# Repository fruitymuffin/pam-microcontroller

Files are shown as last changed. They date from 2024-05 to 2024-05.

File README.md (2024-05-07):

# pam-microcontroller
The AVR controller is based on the AVR64DA32 chip which is programmed via the UPDI interface.

## 1. Compiling
The C/C++ code is compiled using avr-gcc/avr-g++ and makes use of avr-libc. [Microchip Studio](https://www.microchip.com/en-us/tools-resources/develop/microchip-studio) was used as the IDE as it integrates the avr-g++ toolchain so building is easy.

## 2. Uploading
The serialUPDI interface was used to upload .hex or .elf files to the chip with the help of [avrdude](https://github.com/avrdudes/avrdude). An avrdude upload command can be added to Microchip Studio as a external tool to make uploading executables easier.
Go to Tools->External Tools and add a new tool. The tool was configured as:

Command:
```
C:\Program Files\avrdude-v7.3-windows-x64\avrdude.exe
```
Arguments:
```
-p avr64da32 -P COM5 -b 115200 -c serialupdi -C "C:\Program Files\avrdude-v7.3-windows-x64\avrdude.conf" -U flash:w:$(BinDir)\led-controller.hex:i
```

Initial Directory:
```
$(BinDir)
```

In order to set fuses with avrdude on the newer DA series chips, it was necessary to manually write it. Luckily the corrent fuse locations are specified in avrdude.conf under the DX family information. To enable the reset pin, the fuse was written by:
```
avrdude -c serialupdi -p avr64da32 -P com5 -U syscfg0:w:0xC8:m
```

## 3. Serial communication
The avr controller has a FTDI 230XS usb to serial chip. Which will typically show up as /dev/ttyUSBn on linux. To write to the port, we can open it as a file using fopen, however to do so we need to know which tty port our device is on. The device is not guaranteed to always be /dev/ttyUSB0.
To be able to access it consistently we can create a symlink to a known filename by creating a udev rule.

Create a file caled "N-my-rule.rules" in ```/etc/udev/rules.d/``` with the contents:
```
SUBSYSTEM=="tty", ATTRS{idVendor}=="0403", ATTRS{idProduct}=="6015", ATTRS{serial}=="DU0D13LG", SYMLINK+="ttypam-serial"
```

This creates a symlink called ```ttypam-serial``` to the tty port which matches the properties given (idVendor, idProduct, serial), so that we can now use ```/dev/ttypam-serial``` to access our device.

To get the required USB device info use:
```
udevadm info -a -n /dev/ttyUSB0 | grep '{serial}\|{idProduct}\|{idVendor}' | head -n3
```
Where ttyUSB0 is replaced with the tty port of the device. See ```lsusb```.

It might also be necessary to add the user to the dialout group to get permissions to usb devices.

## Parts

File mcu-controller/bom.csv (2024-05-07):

Reference | Value | Datasheet | Footprint | Qty | DNP
C1,C5,C6,C7,C12,C13,C15,C16,C17 | 0.1u | ~ | Capacitor_SMD:C_0805_2012Metric | 9
C2,C3 | 4.7u | ~ | Capacitor_SMD:C_0805_2012Metric | 2
C4 | 0.22u | ~ | Capacitor_SMD:C_0805_2012Metric | 1
C8 | 10u | ~ | Capacitor_SMD:C_1206_3216Metric | 1
C9,C10 | 47p | Tantalum | Capacitor_SMD:C_0805_2012Metric | 2
C11,C14 | 1u | ~ | Capacitor_SMD:C_0805_2012Metric | 2
D1 | LED | ~ | LED_SMD:LED_0805_2012Metric | 1
D2 | RXLED | ~ | LED_SMD:LED_0805_2012Metric | 1
D3 | TXLED | ~ | LED_SMD:LED_0805_2012Metric | 1
J1 | 0534260210 | ~ | Library:CON_534260210_MOL | 1
J2 | HR10A-7R-6SB(73) | ~ | Library:HR10A-7R-6SB(73) | 1
J3 | Conn_01x13 | ~ | Connector_PinHeader_2.54mm:PinHeader_1x13_P2.54mm_Vertical | 1
J4 | 0534260610 | ~ | Library:CON_534260610_MOL | 1
J5,J6 | Conn_01x03 | ~ | Connector_PinHeader_2.54mm:PinHeader_1x03_P2.54mm_Vertical | 2
J7 | 65100516121 | ~ | Connector_USB:USB_Mini-B_Wuerth_65100516121_Horizontal | 1
R1 | 1k | ~ | Resistor_SMD:R_0805_2012Metric | 1
R2,R5 | 4.7k | ~ | Resistor_SMD:R_0805_2012Metric | 2
R3,R4 | 27 | ~ | Resistor_SMD:R_0805_2012Metric | 2
R6 | 10k | ~ | Resistor_SMD:R_0805_2012Metric | 1
R7 | 330 | ~ | Resistor_SMD:R_0805_2012Metric | 1
R8,R9 | 270 | ~ | Resistor_SMD:R_0805_2012Metric | 2
SW1 | SW_Push | ~ | Button_Switch_SMD:SW_SPST_FSMSM | 1
U1 | LM340SX-5.0 | https://www.analog.com/media/en/technical-documentation/data-sheets/112935ff.pdf | Package_TO_SOT_SMD:TO-263-3_TabPin2 | 1
U2 | FT230XS | https://www.ftdichip.com/Support/Documents/DataSheets/ICs/DS_FT230X.pdf | Package_SO:SSOP-16_3.9x4.9mm_P0.635mm | 1
U3 | MCP4822 | http://ww1.microchip.com/downloads/en/DeviceDoc/20002249B.pdf | Package_SO:SOIC-8_3.9x4.9mm_P1.27mm | 1
U4 | AVR64DA32x-xPT | https://ww1.microchip.com/downloads/en/DeviceDoc/AVR64DA28-32-48-64-Data-Sheet-40002233B.pdf | Package_QFP:TQFP-32_7x7mm_P0.8mm | 1

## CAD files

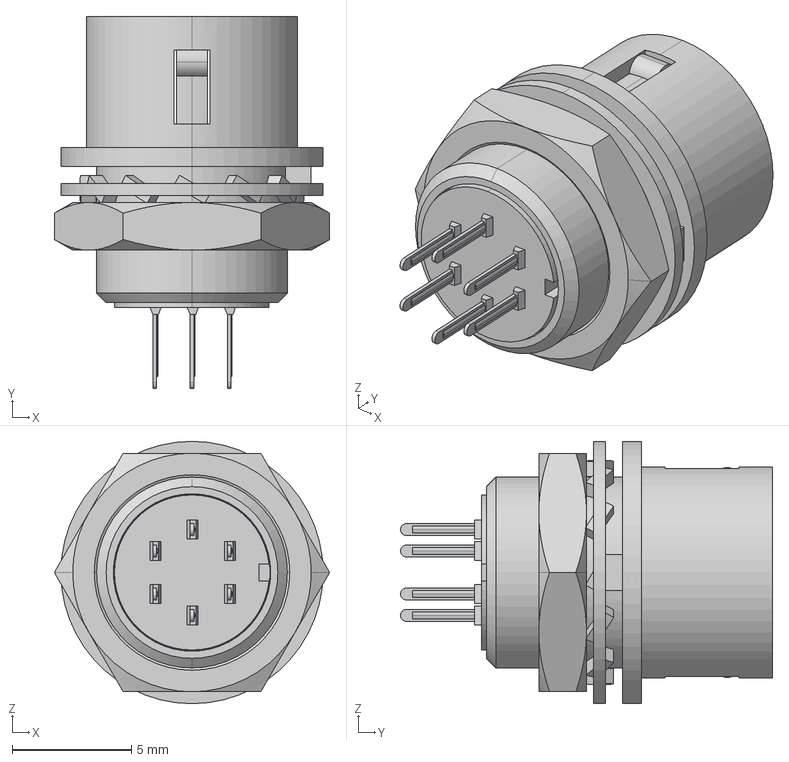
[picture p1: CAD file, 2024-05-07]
mcu-controller/models/HR10A-7R-6PB.stp
11.5 x 15.6 x 11.0 mm

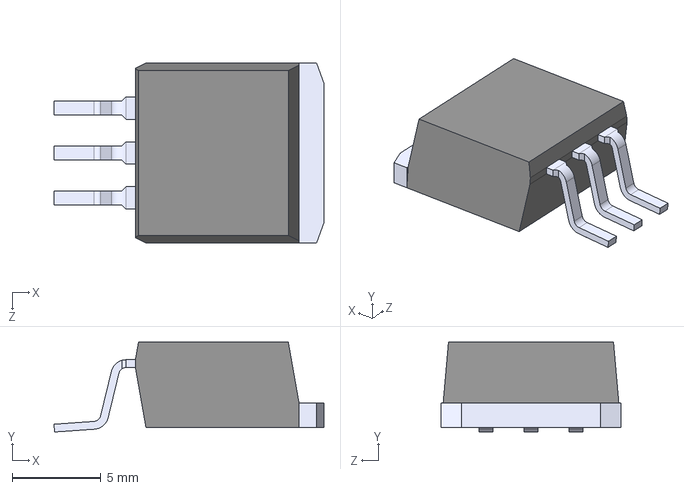
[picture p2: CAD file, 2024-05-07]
mcu-controller/models/LM340SX-5.0_NOPB.step
15.2 x 5.08 x 10.2 mm

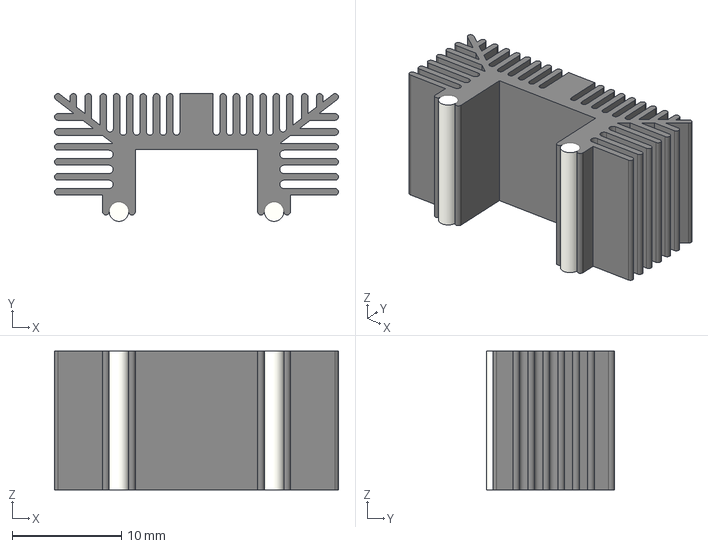
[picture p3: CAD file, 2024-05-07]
mcu-controller/models/ohmite_DA-T263-401E-TR.stp
26.0 x 11.7 x 12.7 mm

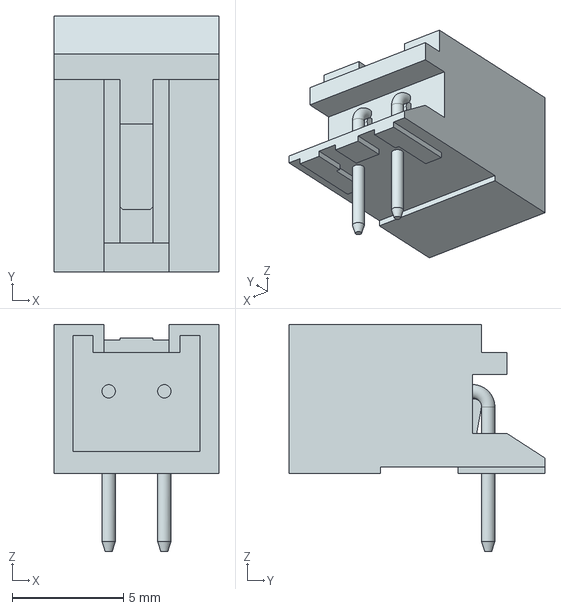
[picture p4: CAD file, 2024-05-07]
mcu-controller/models/534260210.stp
7.40 x 11.5 x 10.2 mm

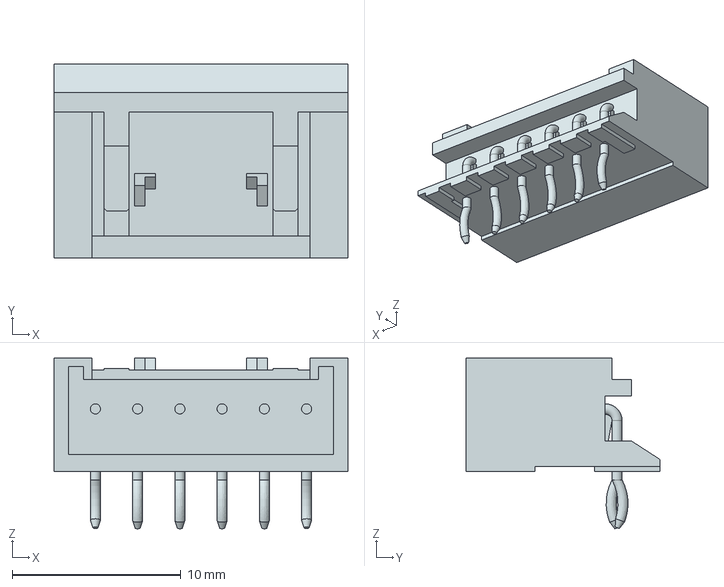
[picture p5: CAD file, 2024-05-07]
mcu-controller/models/534260610.stp
17.4 x 11.5 x 10.1 mm

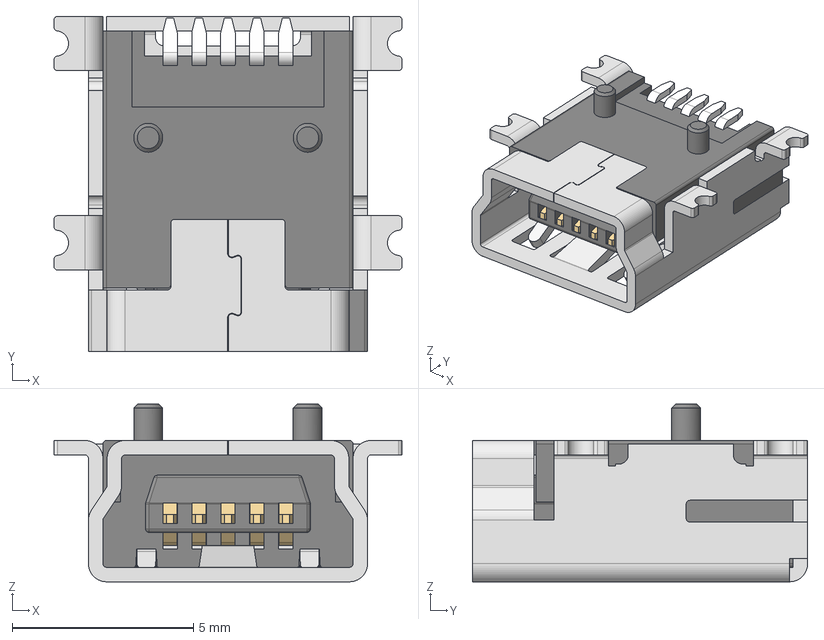
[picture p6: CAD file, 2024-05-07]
mcu-controller/models/65100516121.stp
9.60 x 9.25 x 4.90 mm
Shielding
Insulator
Pin_1 x 5

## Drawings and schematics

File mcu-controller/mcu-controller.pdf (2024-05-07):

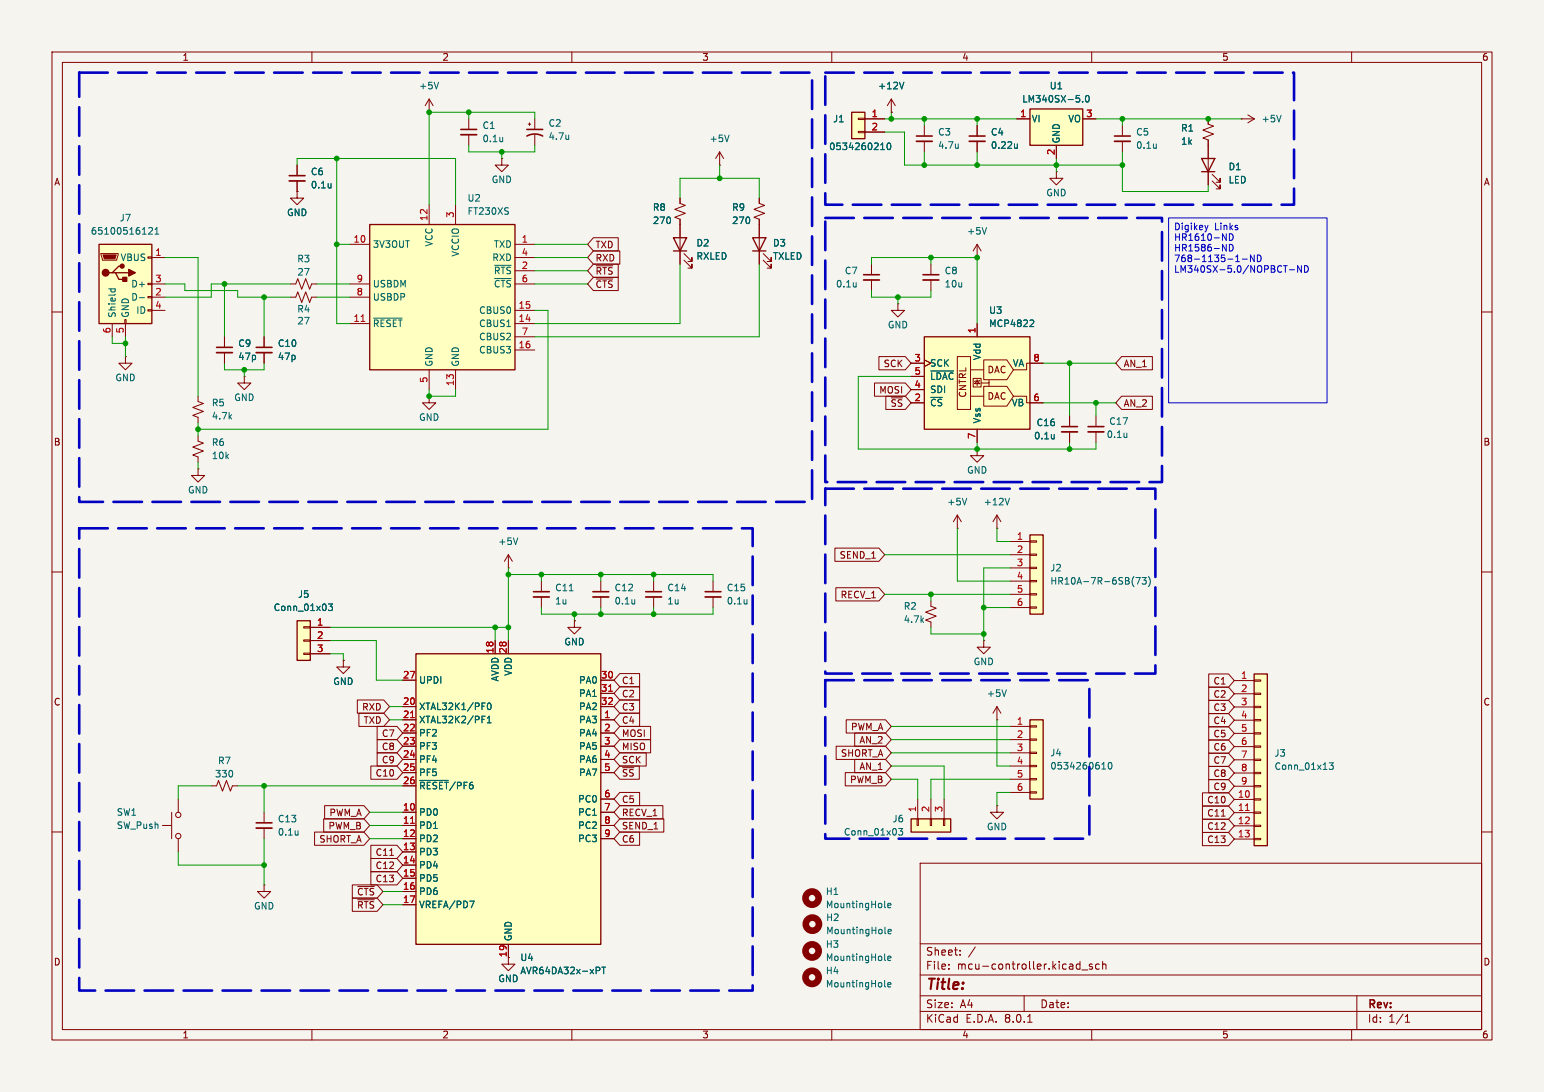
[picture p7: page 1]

1 ~{CS} 2 SCK 3 SDI 4 ~{LDAC} 5 VB 6 Vss 7 VA 8 +12V D1

1 ~{CS} 2 SCK 3 SDI 4 ~{LDAC} 5 VB 6 Vss 7 VA 8 U3 GND MCP4822 GND GND

Id: 1/1 Title: File: mcu-controller.kicad_sch Sheet: /

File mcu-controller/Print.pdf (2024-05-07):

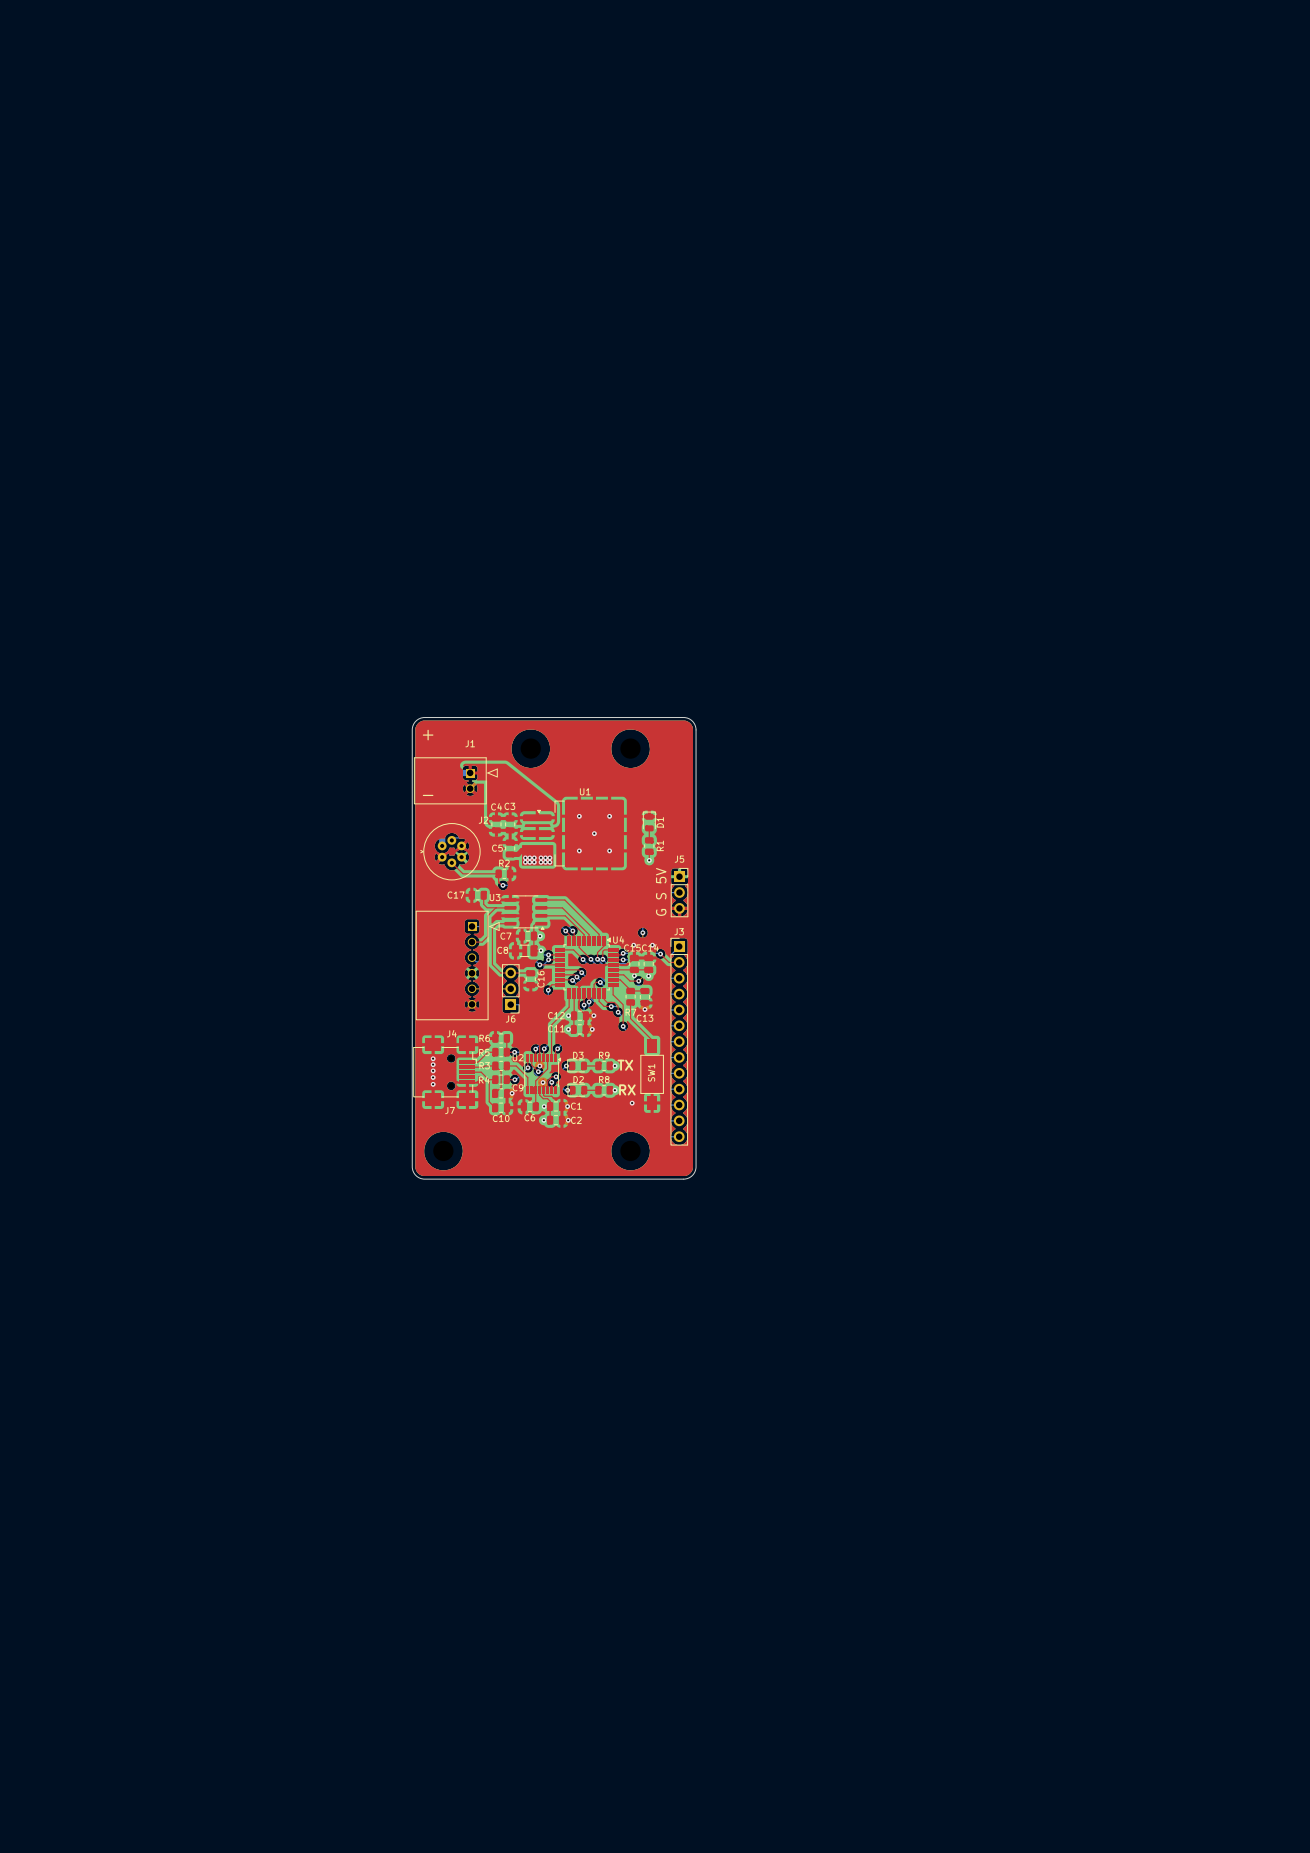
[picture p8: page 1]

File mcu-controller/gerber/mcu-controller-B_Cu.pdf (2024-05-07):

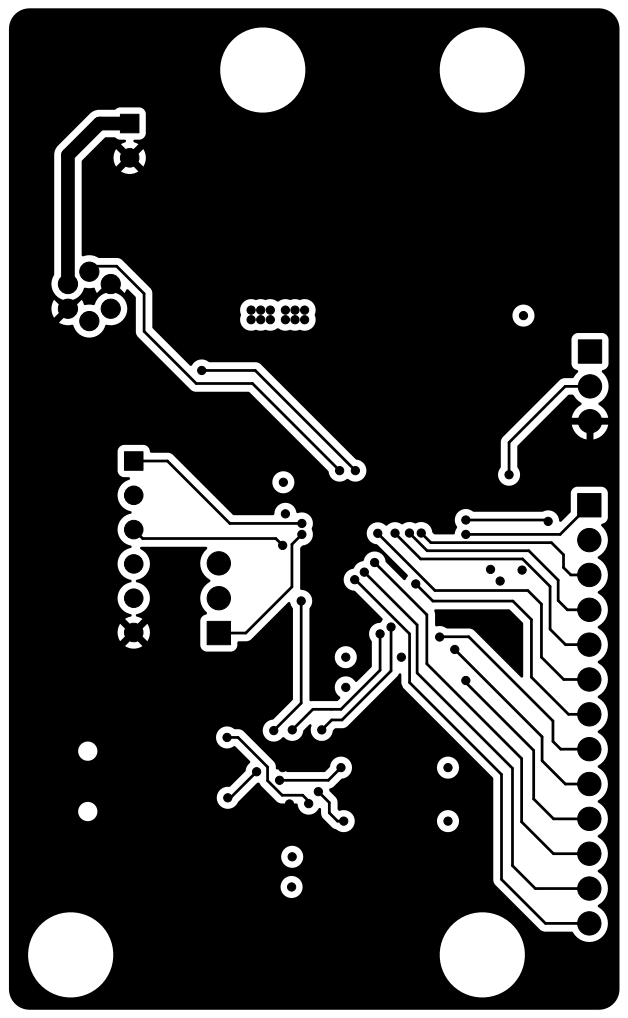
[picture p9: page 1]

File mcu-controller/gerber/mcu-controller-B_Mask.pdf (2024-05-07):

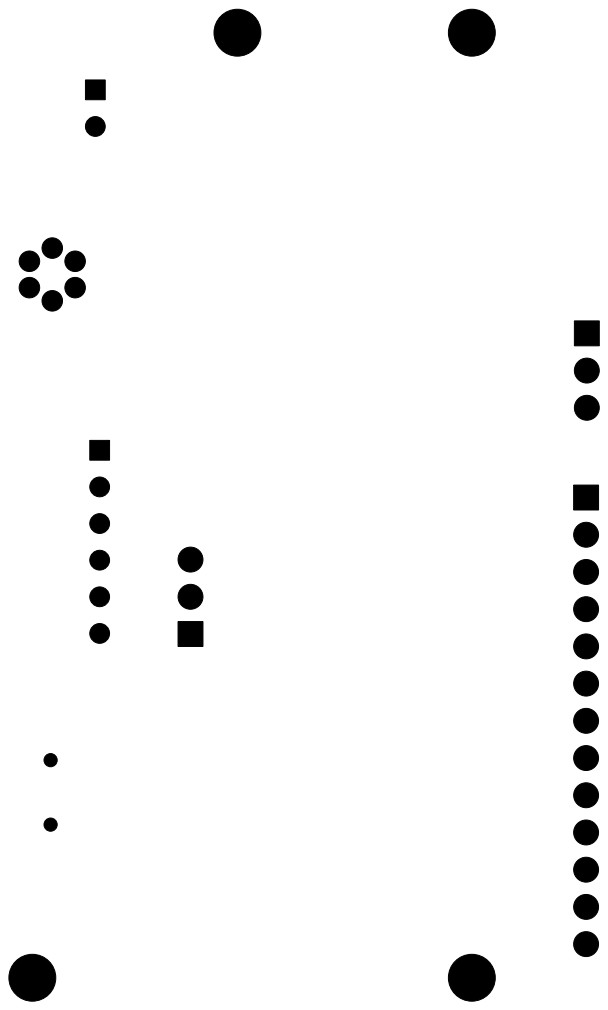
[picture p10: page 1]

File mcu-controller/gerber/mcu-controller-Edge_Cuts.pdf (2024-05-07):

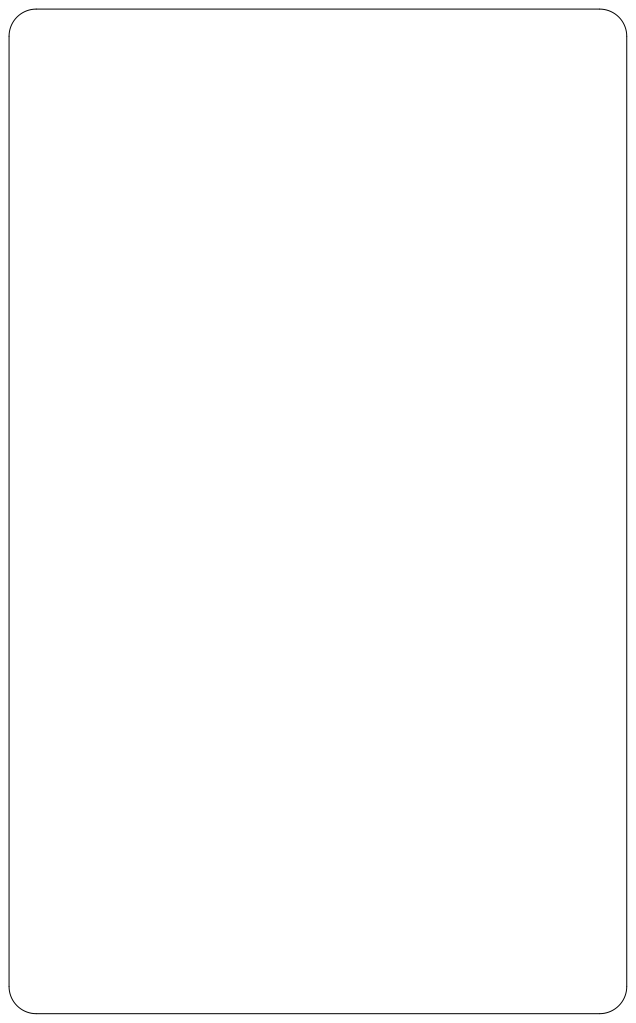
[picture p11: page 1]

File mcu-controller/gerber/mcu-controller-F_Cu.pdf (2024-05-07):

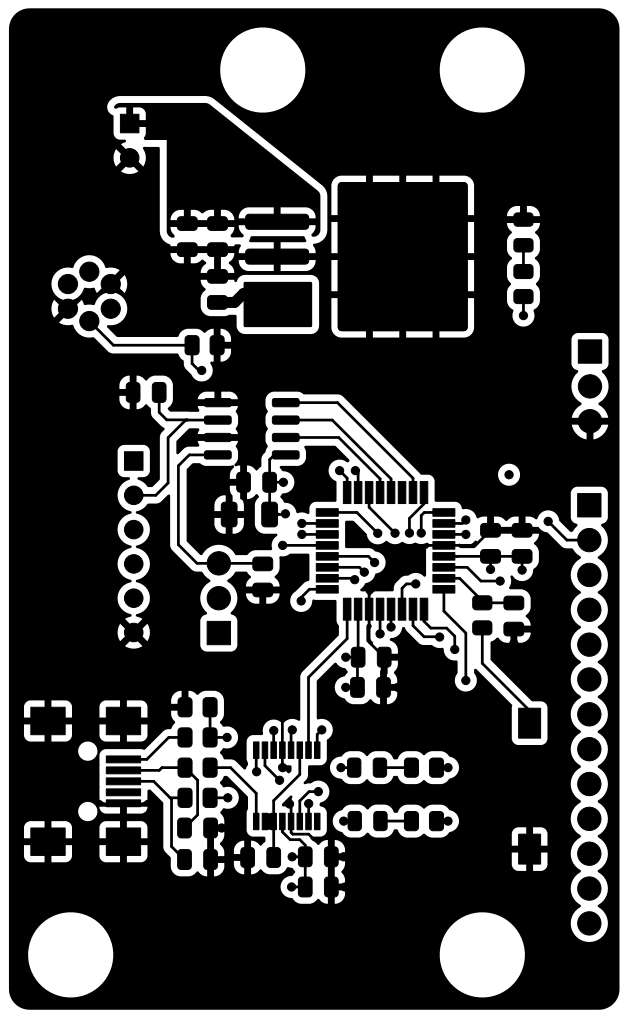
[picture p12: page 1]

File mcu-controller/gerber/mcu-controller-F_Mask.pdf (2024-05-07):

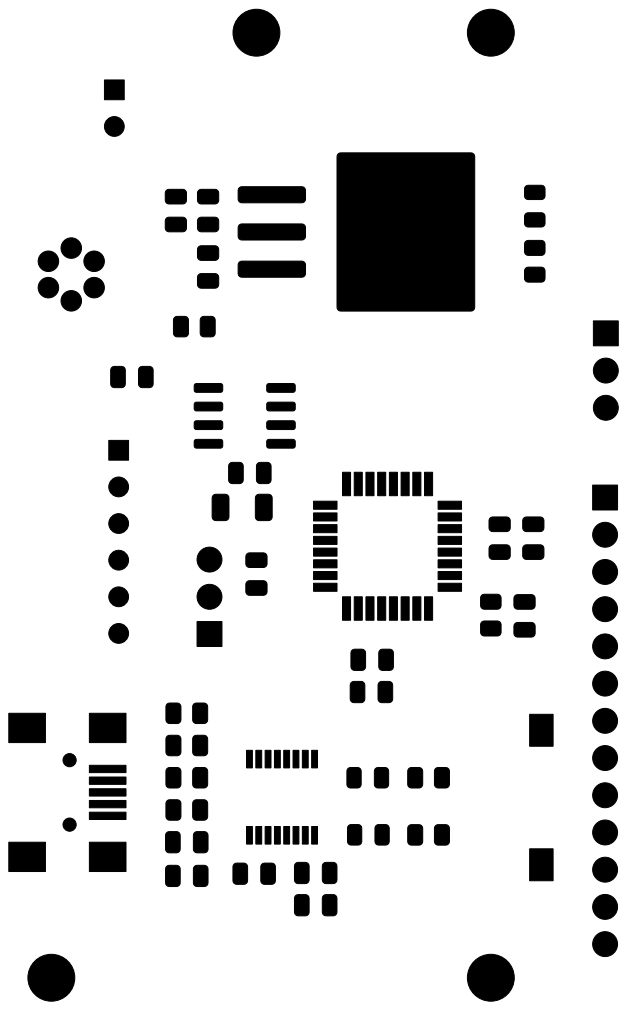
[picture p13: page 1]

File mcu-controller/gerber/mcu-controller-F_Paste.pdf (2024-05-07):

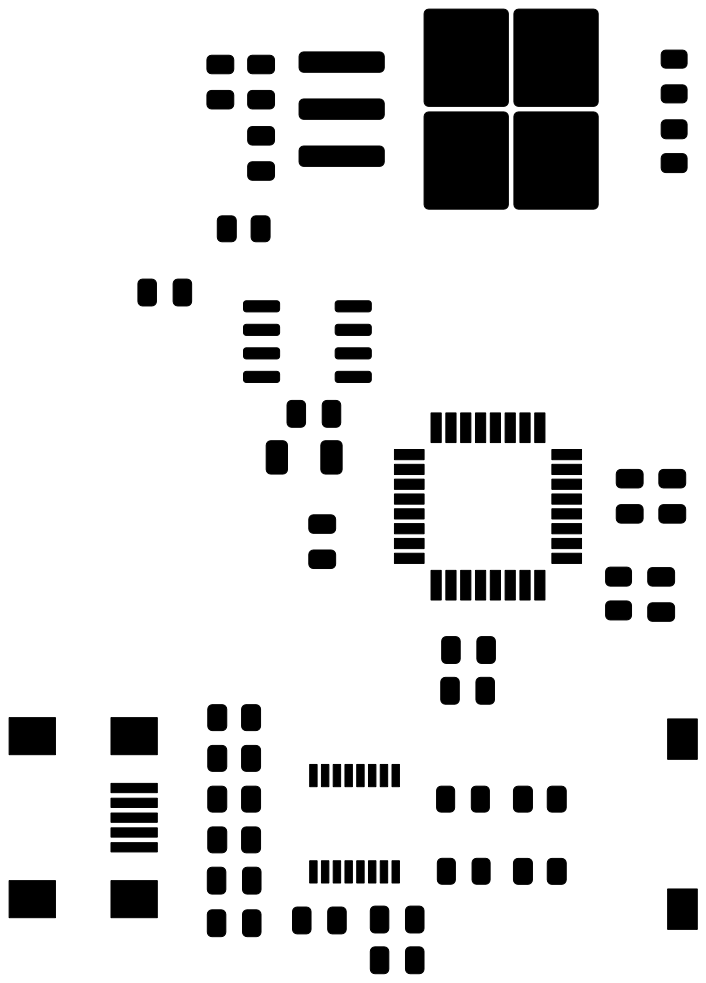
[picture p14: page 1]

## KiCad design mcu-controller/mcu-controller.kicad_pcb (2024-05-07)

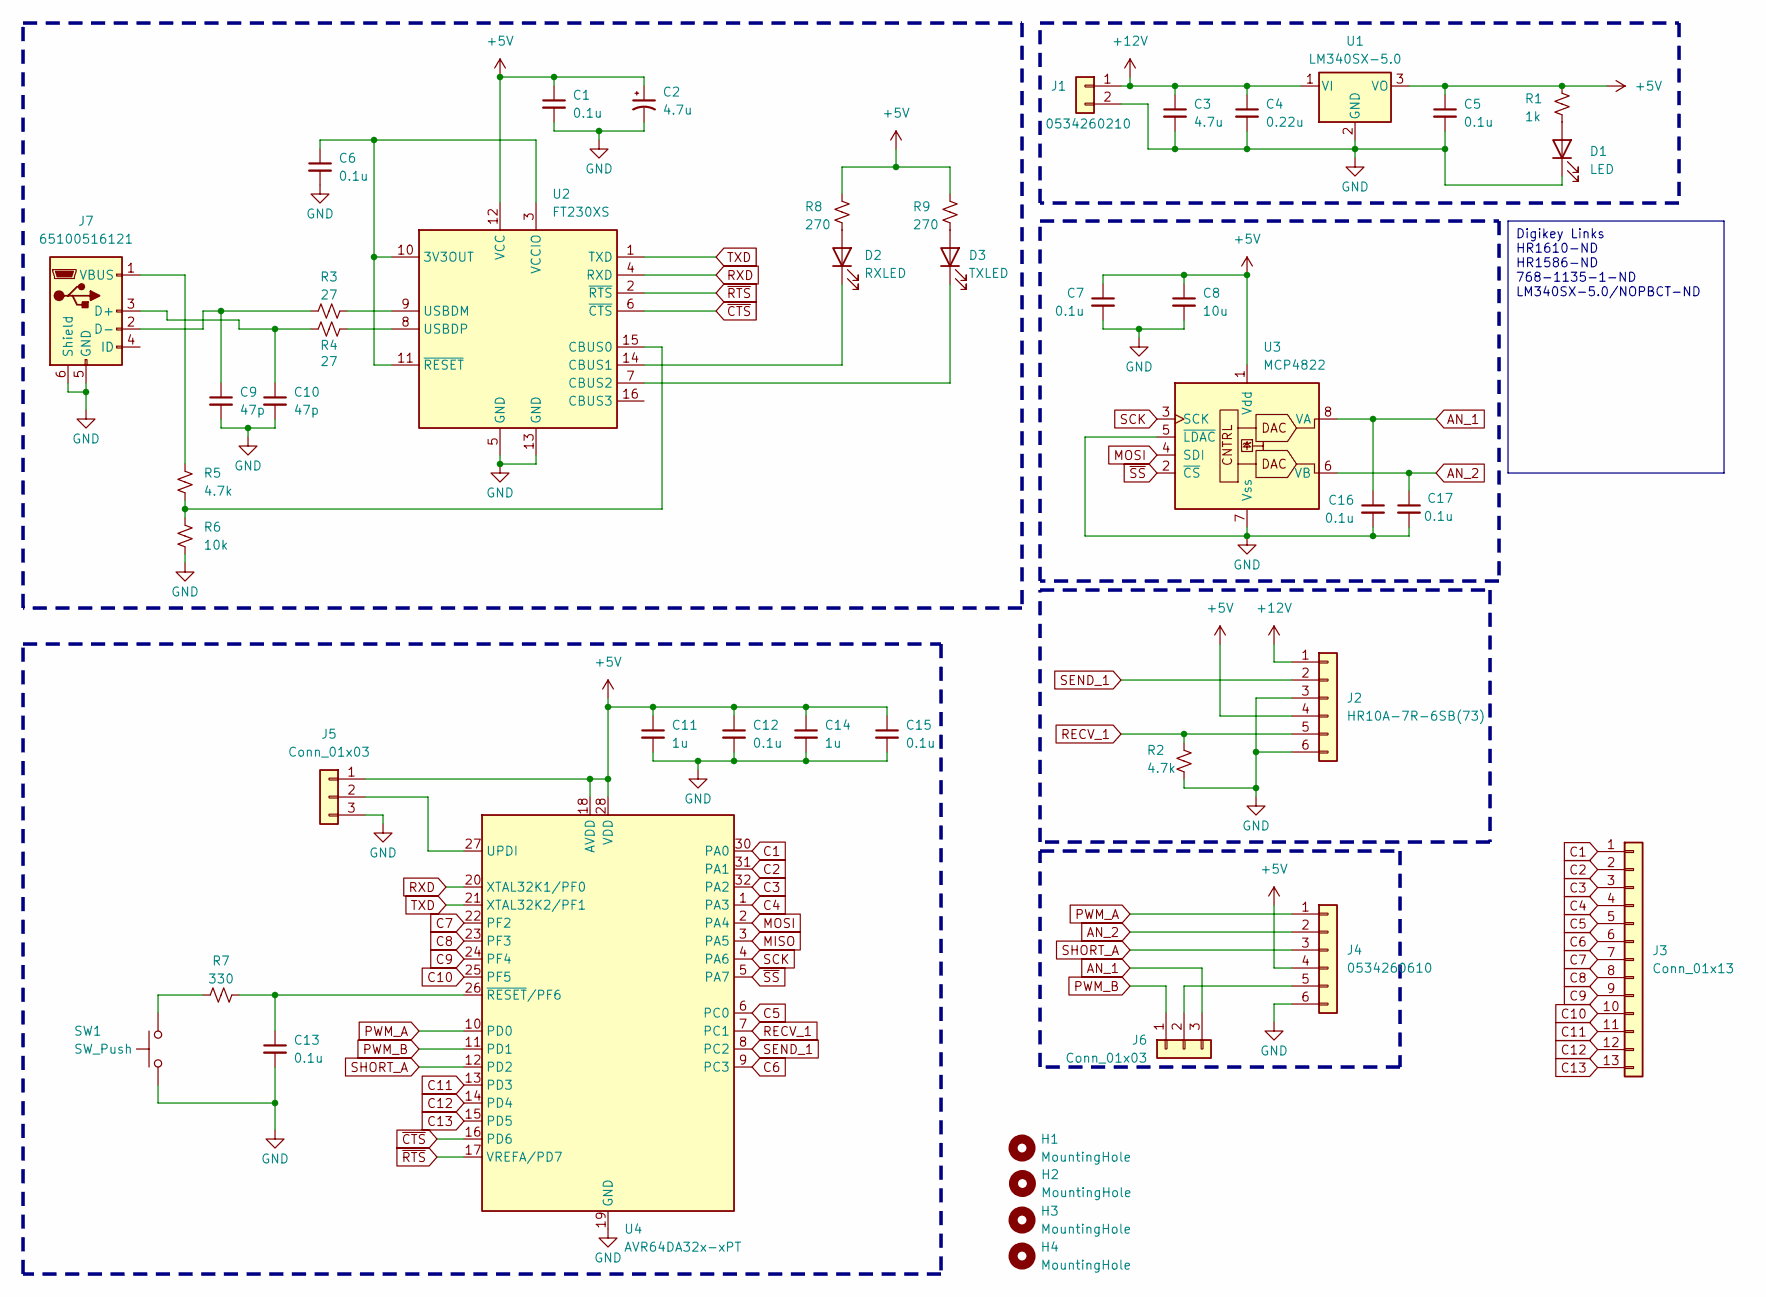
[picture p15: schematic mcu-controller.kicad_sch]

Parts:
C1, C5, C6, C7, C12, C13, C15, C16, C17: 0.1u; C_0805_2012Metric
C2, C3: 4.7u; C_0805_2012Metric
C4: 0.22u; C_0805_2012Metric
C8: 10u; C_1206_3216Metric
C9, C10: 47p; C_0805_2012Metric
C11, C14: 1u; C_0805_2012Metric
D1: LED; LED_0805_2012Metric
D2: RXLED; LED_0805_2012Metric
D3: TXLED; LED_0805_2012Metric
H1, H2, H3, H4: MountingHole; MountingHole_3.2mm_M3
J1: 0534260210; CON_534260210_MOL
J2: HR10A-7R-6SB(73)
J3: Conn_01x13; PinHeader_1x13_P2.54mm_Vertical
J4: 0534260610; CON_534260610_MOL
J5, J6: Conn_01x03; PinHeader_1x03_P2.54mm_Vertical
J7: 65100516121; USB_Mini-B_Wuerth_65100516121_Horizontal
R1: 1k; R_0805_2012Metric
R2, R5: 4.7k; R_0805_2012Metric
R3, R4: 27; R_0805_2012Metric
R6: 10k; R_0805_2012Metric
R7: 330; R_0805_2012Metric
R8, R9: 270; R_0805_2012Metric
SW1: SW_Push; SW_SPST_FSMSM
U1: LM340SX-5.0; TO-263-3_TabPin2
U2: FT230XS; SSOP-16_3.9x4.9mm_P0.635mm
U3: MCP4822; SOIC-8_3.9x4.9mm_P1.27mm
U4: AVR64DA32x-xPT; TQFP-32_7x7mm_P0.8mm

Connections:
+5V: C1.1, C2.1, C5.1, C7.1, C8.1, C11.1, C12.1, C14.1, C15.1, J2.4, J4.4, J5.1, R1.1, R8.1, R9.1, U1.3 (VO), U2.12 (VCC), U3.1 (Vdd), U4.18 (AVDD), U4.28 (VDD)
+12V: C3.1, C4.1, J1.1, J2.1, U1.1 (VI)
AN_1: C16.1, J6.3, U3.8 (VA)
AN_2: C17.1, J4.2, U3.6 (VB)
C1: J3.1, U4.30 (PA0)
C2: J3.2, U4.31 (PA1)
C3: J3.3, U4.32 (PA2)
C4: J3.4, U4.1 (PA3)
C5: J3.5, U4.6 (PC0)
C6: J3.6, U4.9 (PC3)
C7: J3.7, U4.22 (PF2)
C8: J3.8, U4.23 (PF3)
C9: J3.9, U4.24 (PF4)
C10: J3.10, U4.25 (PF5)
C11: J3.11, U4.13 (PD3)
C12: J3.12, U4.14 (PD4)
C13: J3.13, U4.15 (PD5)
GND: C1.2, C2.2, C3.2, C4.2, C5.2, C6.2, C7.2, C8.2, C9.2, C10.2, C11.2, C12.2, C13.2, C14.2, C15.2, C16.2, C17.2, D1.1 (K), J1.2, J2.3, J2.6, J4.6, J5.3, J7.5 (GND), J7.6 (Shield), R2.2, R6.2, SW1.1, U1.2 (GND), U2.5 (GND), U2.13 (GND), U3.5 (~LDAC), U3.7 (Vss), U4.19 (GND), U4.29 (GND)
MISO: U4.3 (PA5)
MOSI: U3.4 (SDI), U4.2 (PA4)
unnamed: D1.2 (A), R1.2
unnamed: D2.2 (A), R8.2
unnamed: D2.1 (K), U2.14 (CBUS1)
unnamed: D3.2 (A), R9.2
unnamed: D3.1 (K), U2.7 (CBUS2)
unnamed: J4.5, J6.2
unnamed: J5.2, U4.27 (UPDI)
unnamed: C10.1, J7.3 (D+), R4.1
unnamed: C9.1, J7.2 (D-), R3.1
unnamed: J7.1 (VBUS), R5.1
unnamed: R7.1, SW1.2
unnamed: C6.1, U2.3 (VCCIO), U2.10 (3V3OUT), U2.11 (~RESET)
unnamed: R5.2, R6.1, U2.15 (CBUS0)
unnamed: R3.2, U2.9 (USBDM)
unnamed: R4.2, U2.8 (USBDP)
unnamed: C13.1, R7.2, U4.26 (~RESET/PF6)
PWM_A: J4.1, U4.10 (PD0)
PWM_B: J6.1, U4.11 (PD1)
RECV_1: J2.5, R2.1, U4.7 (PC1)
RXD: U2.4 (RXD), U4.20 (XTAL32K1/PF0)
SCK: U3.3 (SCK), U4.4 (PA6)
SEND_1: J2.2, U4.8 (PC2)
SHORT_A: J4.3, U4.12 (PD2)
TXD: U2.1 (TXD), U4.21 (XTAL32K2/PF1)
~CTS: U2.6 (~CTS), U4.16 (PD6)
~RTS: U2.2 (~RTS), U4.17 (VREFA/PD7)
~SS: U3.2 (~CS), U4.5 (PA7)

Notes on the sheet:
Digikey Links HR1610-ND HR1586-ND 768-1135-1-ND LM340SX-5.0/NOPBCT-ND

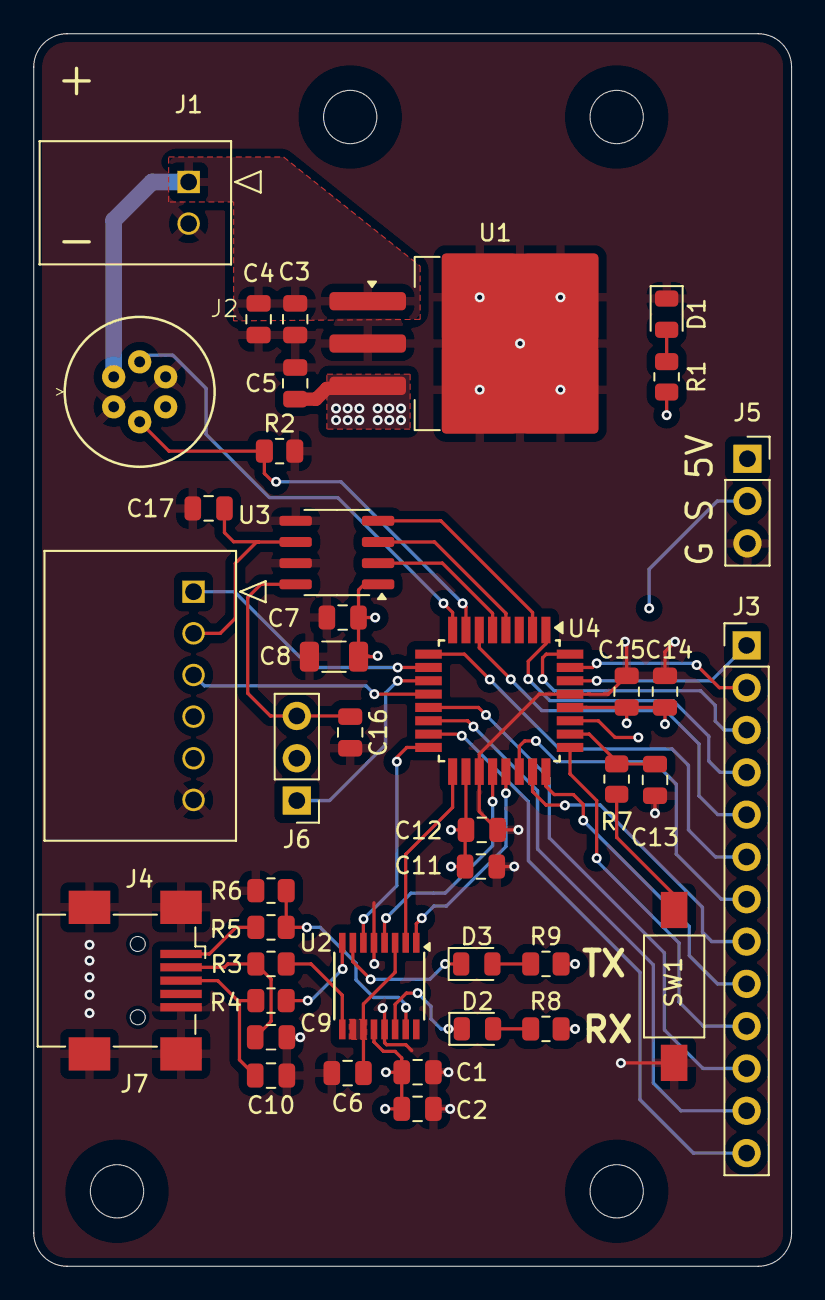
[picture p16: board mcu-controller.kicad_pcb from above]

Board: 4 copper layers, 45.5 x 74.0 mm, 45 parts (0 on the bottom side), 46 nets.

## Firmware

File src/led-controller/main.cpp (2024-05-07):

/*
 * led-controller.cpp
 *
 * Created: 16/04/2024 7:16:16 PM
 * Author : jmcna
 */ 

// Clock params
#define F_CPU 8000000UL

#include <avr/io.h>
#include <avr/interrupt.h>
#include <util/delay.h>
#include <math.h>
#include <stdlib.h>
#include <string.h>
#include <stdio.h>
#include <errno.h>

// USART 2 params
#define USART_BAUD_RATE(BAUD_RATE) ((float)(8000000UL * 64 / (16 * (float)BAUD_RATE)) + 0.5)
#define MAX_INPUT_LEN 512
#define MAX_NUM_COMMANDS 128
#define MAX_NUM_INTS 3*MAX_NUM_COMMANDS

// Analog out params
#define DAC_BLUE 1
#define DAC_WHITE 0

// Timer params
#define TCB0_TOP 0x0190
#define TCB1_TOP 0x4E20
#define TCB2_TOP 0x0FA0

// LED params
#define MAX_AVG_CURRENT  2067 // mA
#define MAX_V_SET        2400 // mV
#define CURRENT_SLEW     200   // mA/us
inline uint8_t getShortTime(const uint16_t& vset) {return vset * MAX_AVG_CURRENT / MAX_V_SET / CURRENT_SLEW;}

// Globals
uint16_t dac_white_value = 0;
uint16_t dac_blue_value = 0;
volatile uint32_t time = 0; // (us)
uint16_t white_led_on_time = 0; // (ms)
uint16_t white_led_brightness = 320; // DAC value

// These are the specific actions that
enum Action
{
	WRITE_DAC_WHITE,
	WRITE_DAC_BLUE,
	BLUE_PULSE,
	WHITE_PULSE,
	SET_DAC_WHITE,
	TRIGGER_PULSE
};

struct Command
{
	int action;
	uint32_t time;
	uint32_t value;
};

void CLOCK_init()
{
	// Set internal oscillator at 8Mhz with autotune enabled
	_PROTECTED_WRITE(CLKCTRL.OSCHFCTRLA, CLKCTRL_FRQSEL_8M_gc);

	// Enable 32KHz RTC to work with autotune
	//_PROTECTED_WRITE(CLKCTRL.XOSC32KCTRLA,  CLKCTRL_ENABLE_bm);

	// Don't enable the clock prescale
	_PROTECTED_WRITE(CLKCTRL.MCLKCTRLB, ~(CLKCTRL_PEN_bm));

	// Select internal HF oscillator
	_PROTECTED_WRITE(CLKCTRL.MCLKCTRLA, CLKCTRL_CLKSEL_OSCHF_gc);
}

void USART2_sendChar(char c)
{
	// Wait until transmit data register is empty
	while (!(USART2.STATUS & USART_DREIF_bm))
	{
		;
	}
	
	// Send data
	USART2.TXDATAL = c;
}

// Initialize USART2 in their default pin locations
void USART2_init(uint16_t baud)
{
	PORTF.DIR |= PIN0_bm;
	PORTF.DIR &= ~PIN1_bm;
	
	// Set the baud rate
	USART2.BAUD = uint16_t(USART_BAUD_RATE(baud));
	
	// Enable transmitter and receiver
	USART2.CTRLB |= USART_TXEN_bm | USART_RXEN_bm;
	
	// Set asynchronous, no parity, 8bit data, 1 stop bit
	// This is the default configuration but we set it explicitly for clarity
	USART2.CTRLC |= USART_PMODE0_bm | USART_SBMODE_1BIT_gc | USART_CHSIZE_8BIT_gc;

	// Initial serial garbage makes messages fail if they occur too soon after init
	_delay_ms(32);
}

void SPI0_init()
{
	// Set MOSI, SCK, and SS to output
	PORTA.DIR |= PIN4_bm | PIN6_bm | PIN7_bm;
	
	// Set endianness, master mode, /4 prescale, no clock doubling, SPI enable
	SPI0.CTRLA = ~(SPI_DORD_bm) | SPI_MASTER_bm & (~SPI_CLK2X_bm) | SPI_PRESC_DIV4_gc | SPI_ENABLE_bm;
}

uint8_t SPI0_write(uint8_t data)
{
	SPI0.DATA = data;
	
	while (!(SPI0.INTFLAGS & SPI_IF_bm))
	{
		;
	}
	return SPI0.DATA;
}

void writeDACn(uint16_t n, uint16_t value)
{
	value = value > 4096 ? 4096 : value;

	// Add configuration bits for DAC selection (a/b) and normal operation
	value |= (n >= 0x01) << 15 & ~(0x01 << 13) | 0x01 << 12;

	// Send SPI
	PORTA.OUT &= ~PIN7_bm;
	SPI0_write(value >> 8);
	SPI0_write(value);
	PORTA.OUT |= PIN7_bm;
}

void GPIO_init(void)
{
	// Set the direction of the GPIO pins we use
	PORTD_DIR |= PIN0_bm;	// PWM BLUE
	PORTD_DIR |= PIN1_bm;	// PWM WHITE
	PORTD_DIR |= PIN2_bm;	// SHORT BLUE
	PORTC_DIR |= PIN2_bm;	// TRIGGER
	
	// Set all digital outputs to LOW
	PORTD_OUTCLR = PIN0_bm | PIN1_bm | PIN2_bm;
	PORTC_OUTCLR = PIN2_bm;
	
	writeDACn(DAC_BLUE, 0);
	writeDACn(DAC_WHITE, 0);
}

uint8_t USART2_readChar()
{
	// Wait for unread data in the receive buffer
	while(!(USART2.STATUS & USART_RXCIF_bm))
	{
		;
	}
	
	return USART2.RXDATAL;
}

void USART2_sendString(char *str)
{
	for(size_t i = 0; i < strlen(str); i++)
	{
		USART2_sendChar(str[i]);
	}
}

void USART2_readString(char* str)
{
	USART2_sendString("Started reading\n");
	char c;
	uint8_t index = 0;

	while (1)
	{
		c = USART2_readChar();
		if(c != '\n' && c != '\r')
		{
			str[index++] = c;
		
			// overwrite old data if it overruns the input buffer
			if(index > MAX_INPUT_LEN)
			{
				index = 0;
			}
		}

		if(c == '\n')
		{
			str[index] = '\0';
			index = 0;
			USART2_sendString("char!\n");
			return;
		}
	}
}

bool parse(const char* c, char** end, Command* cmds, size_t& idx)
{
	//printf("Parsing '%s':\n", c);
	uint32_t buffer[MAX_NUM_INTS];
	uint8_t n = 0;
	*end = (char*)c;

	USART2_sendString("Started parsing\n");
	while (n < MAX_NUM_INTS)
	{
		// Reset errno, as its used by many std functions
		errno = 0;

		// Attempt to extract a long from the string
		const uint32_t val = strtoul(c, end, 10);

		// Check if there was a range error
		const bool range_error = errno == ERANGE;

		// Conversion failed, stop
		if (c == *end || range_error)
			break;

		// Update the start of the string to where the last number extracted finished
		c = *end;

		// Add the new number to the buffer
		buffer[n] = val;

		// Increment counter
		n++;
	}

	// Need multiple of 3 to make valid commands
	if (n % 3 != 0 || n == 0)
	{
		return false;
	}

	idx = n / 3;
	for(int i = 0; i < n; i += 3)
	{
		cmds[i/3] = {int(buffer[i]), buffer[i+1], buffer[i+2] };
	}

	return true;
}

void TCB0_init(void)
{
	// Default mode and clock source are OK
	
	// Enable overflow interrupt
	TCB0.INTCTRL = TCB_CAPT_bm;
	
	// Set TOP value to correspond with 50us pulse width
	TCB0.CCMP = TCB0_TOP;
}

void TCB1_init(void)
{
	// Default mode and clock source are OK
	
	// Enable overflow interrupt
	TCB1.INTCTRL = TCB_CAPT_bm;
	
	TCB1.CTRLA |= TCB_CLKSEL_DIV2_gc;
	
	// Set TOP value to correspond with 50us pulse width
	TCB1.CCMP = TCB1_TOP;
}

void TCB2_init(void)
{
	// Default mode and clock source are OK
	
	// Enable compare interrupt
	TCB2.INTCTRL = TCB_CAPT_bm;
	
	TCB2.CTRLA |= TCB_CLKSEL_DIV2_gc;
	
	// Set TOP value for 10us time
	TCB2.CCMP = TCB2_TOP;
	
	// Start
	TCB2.CTRLA |= TCB_ENABLE_bm;
}

void TCA0_init(void)
{
	/* set Normal mode */
	TCA0.SINGLE.CTRLB = TCA_SINGLE_WGMODE_NORMAL_gc;
	
	// Enable count interrupts for both count 0, 1
	TCA0.SINGLE.INTCTRL = TCA_SINGLE_CMP0EN_bm | TCA_SINGLE_CMP1EN_bm;
	/* disable event counting */
	TCA0.SINGLE.EVCTRL &= ~(TCA_SINGLE_CNTAEI_bm);
	// Set prescale
	TCA0.SINGLE.CTRLA = TCA_SINGLE_CLKSEL_DIV1_gc;
}

ISR(TCA0_CMP0_vect)
{
	PORTD_OUTCLR = PIN2_bm;
	TCA0.SINGLE.INTFLAGS |= TCA_SINGLE_CMP0_bm;
}

ISR(TCA0_CMP1_vect)
{
	PORTD_OUTCLR = PIN0_bm;
	TCA0.SINGLE.INTFLAGS |= TCA_SINGLE_CMP1_bm;
	
	TCA0.SINGLE.INTCTRL &= ~TCA_SINGLE_CMP0EN_bm & ~TCA_SINGLE_CMP1EN_bm;
	
	TCA0.SINGLE.CTRLA &= ~TCA_SINGLE_ENABLE_bm;
}

ISR(TCB0_INT_vect)
{
	// Set the trigger low
	PORTC_OUTCLR = PIN2_bm;
	
	// Turn off interrupt
	TCB0.INTFLAGS |= TCB_CAPT_bm;
	TCB0.CTRLA &= ~TCB_ENABLE_bm;
}

ISR(TCB1_INT_vect)
{
	static uint16_t counter = 0;
	
	// Increment time, we have 8Mhz clock with DIV2 prescale so
	// milliseconds = count / 4000
	counter += TCB1_TOP / 4000;
	
	if (counter >= white_led_on_time)
	{
		// Turn off interrupt
		TCB1.INTCTRL = 0;
		
		// Turn off white LED
		writeDACn(DAC_WHITE, 0);
		
		// Reset counter for next time
		counter = 0;
		
		// Disable interrupt
		TCB1.INTCTRL &= ~TCB_CAPT_bm;
	}
	TCB1.INTFLAGS = TCB_CAPT_bm;
}

ISR(TCB2_INT_vect)
{
	// +1 ms
	++time;
	
	// Clear flag
	TCB2.INTFLAGS |= TCB_CAPT_bm;
}

void delayMicroseconds(uint16_t us)
{
	// for the 8 MHz internal clock

	// for a 1 and 2 microsecond delay, simply return.  the overhead
	// of the function call takes 14 (16) cycles, which is 2us
	if (us <= 2) return; //  = 3 cycles, (4 when true)

	// the following loop takes 1/2 of a microsecond (4 cycles)
	// per iteration, so execute it twice for each microsecond of
	// delay requested.
	us <<= 1; //x2 us, = 2 cycles

	// account for the time taken in the preceeding commands.
	// we just burned 17 (19) cycles above, remove 4, (4*4=16)
	// us is at least 6 so we can substract 4
	us -= 4; // = 2 cycles
	
	
	// busy wait
	__asm__ __volatile__ (
	"1: sbiw %0,1" "\n\t" // 2 cycles
	"brne 1b" : "=w" (us) : "0" (us) // 2 cycles
	);
	// return = 4 cycles
}

void pulse(uint8_t tshort, uint32_t ton)
{
	// Reduce tshort by 2us, the overhead in enabling the timer
	if (tshort > 2)
	tshort -= 2;
	else
	tshort = 0;
	
	// Ton could range from 10us to 1000000us in theory. If it is larger than 8191us, change the prescale
	if (ton > (uint16_t(~0) >> 3))
	{
		USART2_sendString("Pulse Big\n");
		// Set prescale to x256 T = 32 (us)
		TCA0.SINGLE.CTRLA = TCA_SINGLE_CLKSEL_DIV256_gc;
		
		// Enable interrupts
		TCA0.SINGLE.INTCTRL = TCA_SINGLE_CMP1EN_bm;
		
		// Set compare value
		TCA0.SINGLE.CMP1 = (tshort + ton) >> 5;
		
		// Enable
		TCA0.SINGLE.CNT = 0;
		TCA0.SINGLE.CTRLA |= TCA_SINGLE_ENABLE_bm;
		
		// Set pins ON
		PORTD_OUTSET = PIN0_bm | PIN2_bm;
		
		// Wait tshort microseconds and turn OFF short
		delayMicroseconds(tshort+2);
		PORTD_OUTCLR = PIN2_bm;
	}
	else
	{
		USART2_sendString("Pulse\n");
		// Enable interrupts
		TCA0.SINGLE.INTCTRL |= TCA_SINGLE_CMP0EN_bm | TCA_SINGLE_CMP1EN_bm;
		
		// Set prescale DIV1
		TCA0.SINGLE.CTRLA = TCA_SINGLE_CLKSEL_DIV1_gc;
		
		// Set compare values
		TCA0.SINGLE.CMP0 = tshort << 3;
		TCA0.SINGLE.CMP1 = (tshort + ton) << 3;
		
		// Enable
		TCA0.SINGLE.CNT = 0;
		TCA0.SINGLE.CTRLA |= TCA_SINGLE_ENABLE_bm;
		
		// Set pins ON
		PORTD_OUTSET = PIN0_bm | PIN2_bm;
	}
}

void execute(Command* cmds, size_t idx)
{
	time = 0;

	uint16_t i = 0;
	while(i < idx)
	{		
		if (cmds[i].time <= time)
		{
			switch (cmds[i].action)
			{
				case WRITE_DAC_WHITE:
					dac_white_value = cmds[i]. value;
					writeDACn(DAC_WHITE, dac_white_value);
					break;
				case WRITE_DAC_BLUE:
					dac_blue_value = cmds[i].value;
					writeDACn(DAC_BLUE, dac_blue_value);
					break;
				case BLUE_PULSE:
					pulse(getShortTime(dac_blue_value), cmds[i].value);
					break;
				case WHITE_PULSE:
					TCB1.CNT = 0x00;
					// Turn on interrupt
					TCB1.INTCTRL = TCB_CAPT_bm;
					
					// Set on time
					white_led_on_time = cmds[i].value;
										
					// Turn on white LED
					writeDACn(DAC_WHITE, white_led_brightness);
					
					// Start timer B
					TCB1.CTRLA |= TCB_ENABLE_bm;
					
					break;
				case SET_DAC_WHITE:
					white_led_brightness = cmds[i].value;
					break;
					
				case TRIGGER_PULSE:
					// Reset timer count and top value
					TCB0_CNT = 0x00;
					
					// Turn on interrupt
					TCB0.INTCTRL = TCB_CAPT_bm;
					
					// Start timer B
					TCB0.CTRLA = TCB_ENABLE_bm;
					
					// Write pin high
					PORTC_OUTSET = PIN2_bm;
					break;
				default:
					break;
			}
			i++;	
		}
	}
}

int main(void)
{
	// Initialise modules
	CLOCK_init();
	SPI0_init();
	GPIO_init();
	TCA0_init();
	TCB0_init();
	TCB1_init();
	TCB2_init();
	USART2_init(9600);
	sei();
			
	// Receive buffer for all commands
	char buffer[MAX_INPUT_LEN];
	Command commands[MAX_NUM_COMMANDS];
	
	while (1)
	{
		// Wait for a line
		USART2_readString(buffer);
		
		char * end;
		size_t idx = 0;
		if ( parse(buffer, &end, commands, idx) )
		{
			USART2_sendString("Good parse!\n");
			for(int i = 0; i < idx; i++)
			{
				sprintf(buffer, "{\n\t%d \n\t%lu \n\t%lu \n}\n", commands[i].action, commands[i].time, commands[i].value);
				USART2_sendString(buffer);
			}
			execute(commands, idx);
		}
		else
		{
			USART2_sendString("Bad parse!\n");
			USART2_sendString(end);
		}
		
	}
}
